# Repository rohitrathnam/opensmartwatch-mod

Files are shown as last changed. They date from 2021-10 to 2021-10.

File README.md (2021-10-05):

# opensmartwatch-mod
openSmartwatch project with an ECG frontend 

Part of course lab Electronic System Design

See Report.pdf for more details.

## Schematic
schematics

## PCB
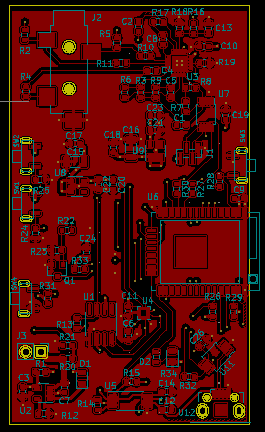
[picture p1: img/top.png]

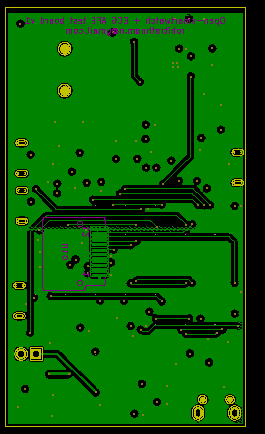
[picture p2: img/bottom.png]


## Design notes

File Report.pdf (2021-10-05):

# IL2237 Lab2 - PCB Design

### Rohit Rathnam Nareshkumar

### May 21, 2021

## 1 Introduction

The aim was to create a development board with the following features:

- A display and buttons to interact with the device
- WiFi / Bluetooth connectivity
- Battery powered with USB charging
- Compact ECG measurement
- Real time clock to keep track of time
- Accelerometer to help with ECG signal processing

The base schematic design that this project is built on is the Open-SmartWatch (OSW) project (1).

## 2 Schematic Design

The Open-SmartWatch schematic is based on an ESP-32 module with support for all of the above except the ECG module. The base schematic is given in Fig 1.
The modified schematic with the ECG circuit is given in Fig 2. The ECG circuit is based on reference design from AD8232 ECG analog front end IC and ADS1015 12-bit ADC.

1

Figure 1: Original schematic

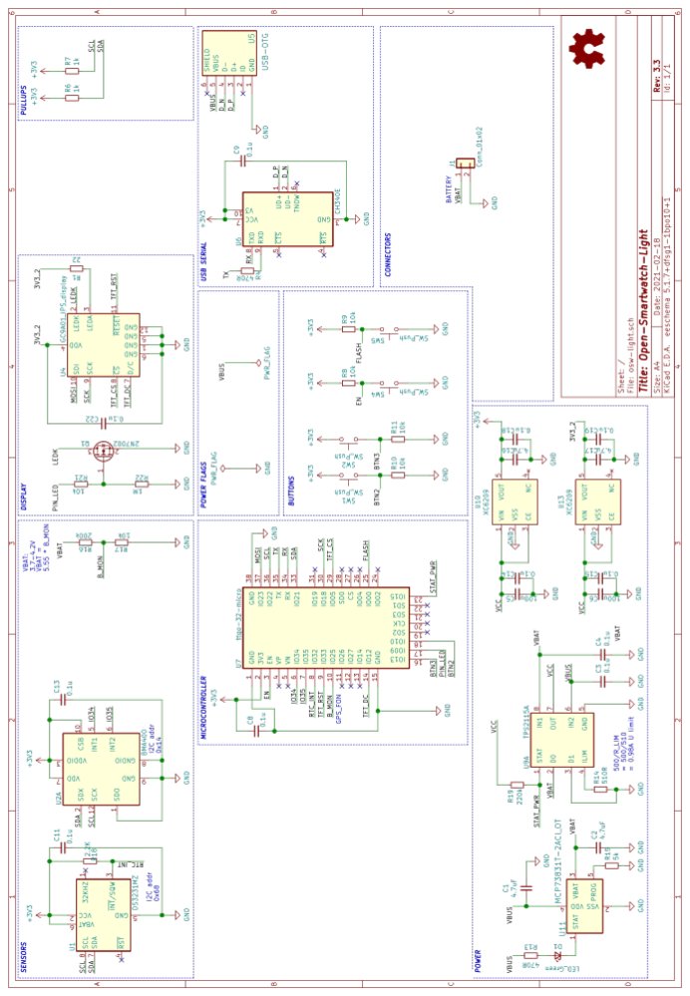
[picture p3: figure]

2

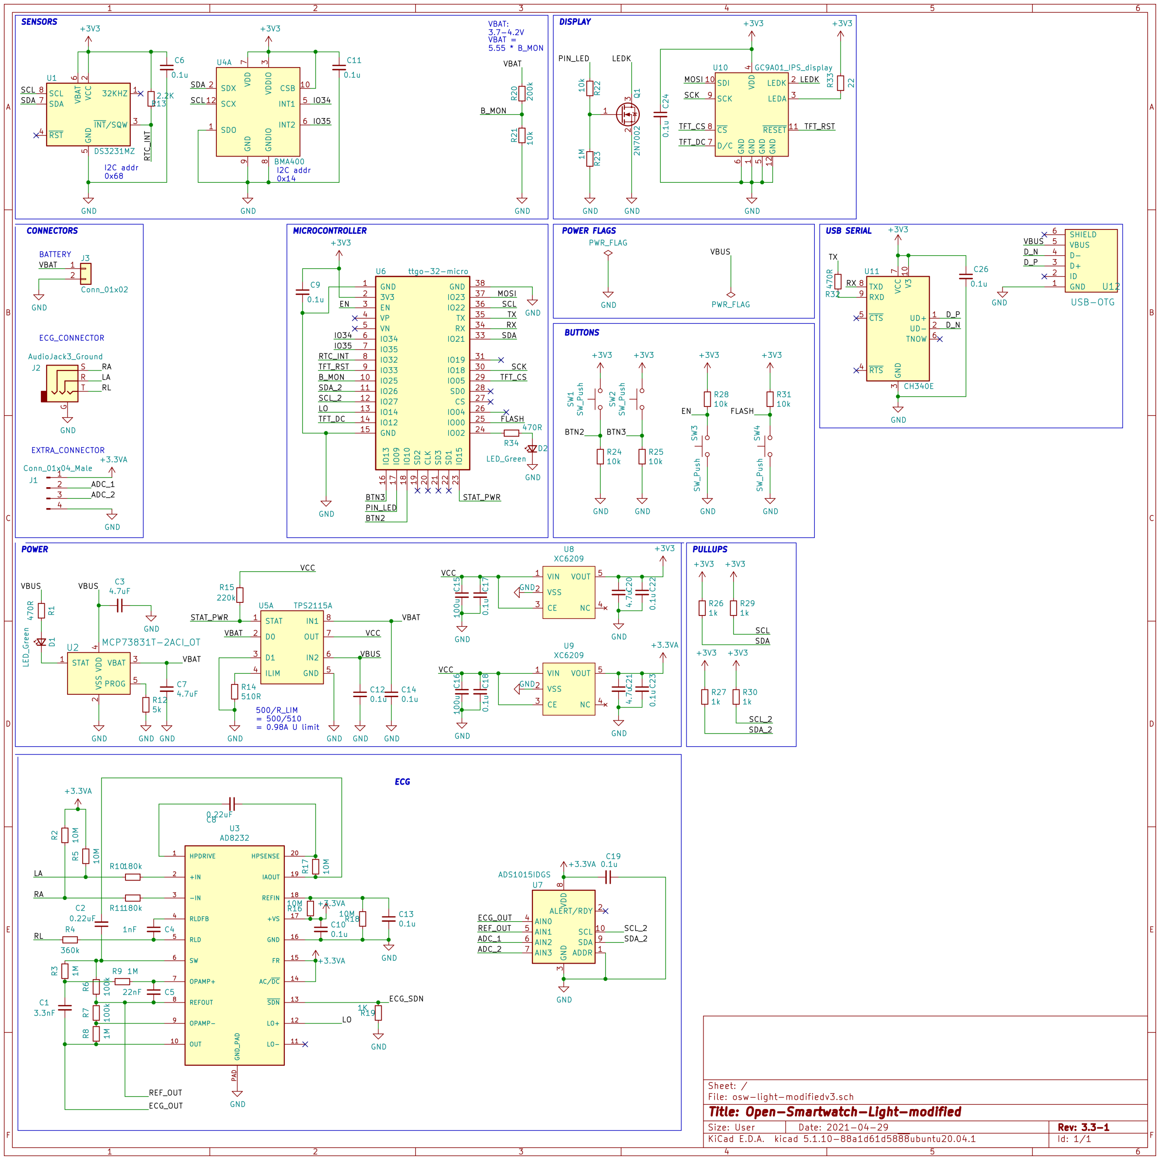
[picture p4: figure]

Figure 2: Modified schematic

3

### 2.1 Microcontroller

The microcontroller used in this project is an ESP-32 variant called the ttgo-32, which has a smaller form factor suitable for smartwatches. It has a PCB antenna and support for WiFi / Bluetooth. The microcontroller also features a low power core, which can be utilised to improve battery life when logging data. The PCB antenna is positioned extending from the edge of the board so that the copper does not interfere with the transmission line. The programming interface is through USB, the device goes into programming mode using the BOOT push button.

### 2.2 Power supply

The power supply consists of a battery management IC (MCP73831) which is responsible for charging the single cell Li battery, current limiting the battery, and producing a regulated output (VBUS). A power line multiplexer (TPS2115A) is used to switch between battery power and USB 5V. The output voltage then goes to two parallel voltage regulators (XC6209) which produce 3V3 and A3V3. Net 3V3 powers all the digital circuits, and A3V3 powers the ECG front end module and ADC. The original design had the display on a separate voltage regulator (possibly due to higher power consumption), but to accommodate a separate analog supply rail, the display was shifted to the digital supply regulator along with the other peripherals and micro-controller. The device can also monitor battery voltage through a voltage divider connected to the internal ADC of the ESP-32.

### 2.3 Display

The display module is a circular IPS display which interfaces over SPI. The module has a FPC connector which is placed on the back of the board to fold the display over the board.

### 2.4 Peripherals

The other peripherals include a BMA400 accelerometer, and a real-time clock both connected via I2C to the ESP-32. Push buttons were given for boot, turning on display and two buttons with software defined functions. A power LED

4

### 2.5 ECG module and ADC

The ECG module (AD8232) and 12-bit ADC (ADS1015) are powered by A3V3 net. The input to the ECG module is through a 3-pin 3.5mm audio jack interface. This can connect to an off the shelf module for ECG leads (2). The design for this section was adapted from the application note given in the datasheet (3). The ECG module has a differential output, which is connected to the two of the ADC input pins. Additional safety mechanism such as ESD diodes, fuses etc. were ignored due to additional complexity in schematic design, which was beyond the scope of this lab. The two extra inputs to the ADC were broken out along with A3V3 and GND to a 1mm pin header for future use. The ADC interfaces with the microcontroller over I2C, and was connected to a dedicated I2C pins so the accelerometer and ADC readings can be polled simultaneously do aid ECG signal processing and motion noise removal.

## 3 Layout considerations

The major factors considered was in the placement of USB connector and routing of USB differential pair, proper clearance for the antenna section of the ESP-32, and proper routing and placement of components for the ECG IC and ADC. For this design, I decided to go with a 4 layer board to allow for ground and power planes. Since this was a development board, there is not much size constraint, as such I tried to stick with a credit card size as a starting point. The final dimensions of the board is 70mm x 40mm.

### 3.1 Component placement

- Priority was given to routing the differential pair to the USB IC from the connector at the edge of the board. The traces were calculated using the KiCAD PCBcalculator tool shown in Fig. 4.
- Decoupling capacitors for all of the devices were placed as close as possible to the supply pins and vias connected to the respective layers.
- The ECG IC and the ADC were placed in a separate section of the board to minimise noise. A split ground plane was avoided for simplicity. The trace length and layer changes were minimised as much as possible.
- Signal traces were 0.25mm wide and power traces were 0.5mm / 1mm

5

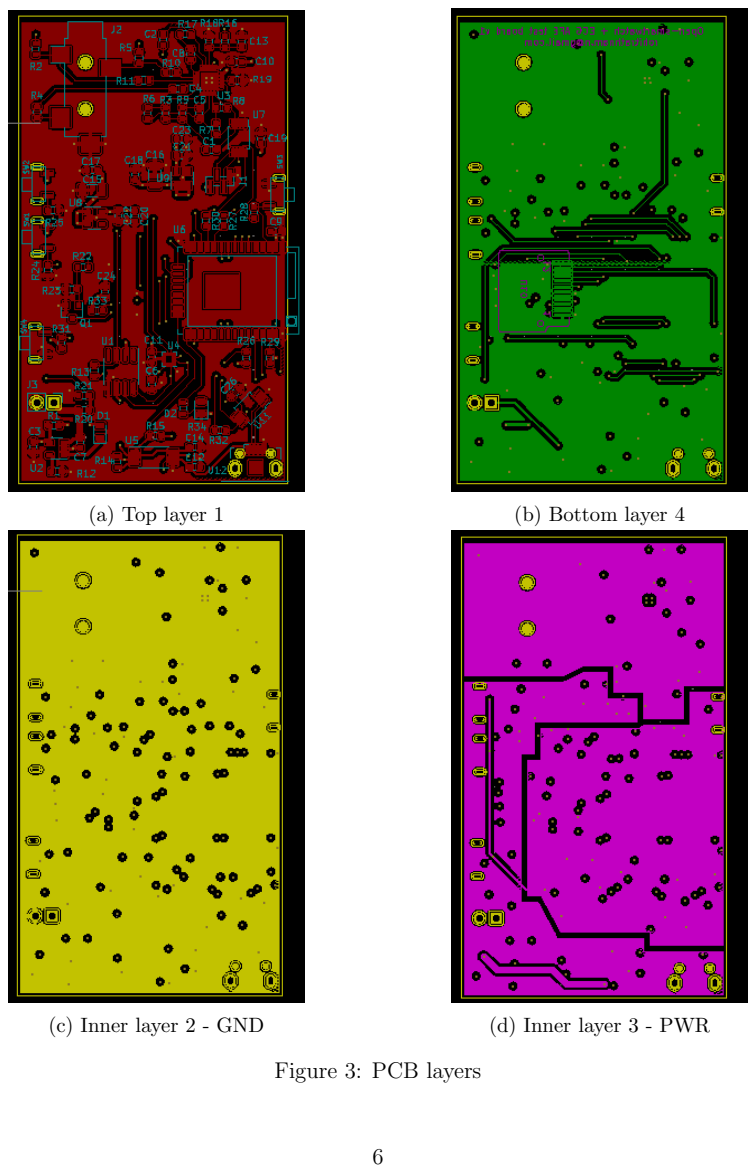
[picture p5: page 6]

(a) Top layer 1 | (b) Bottom layer 4
(c) Inner layer 2 - GND | (d) Inner layer 3 - PWR

Figure 3: PCB layers

6

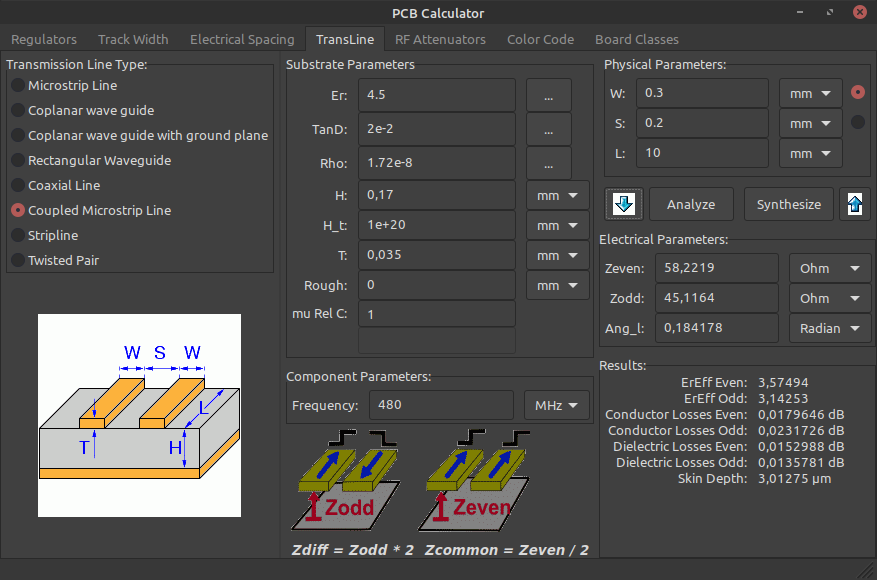
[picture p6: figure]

Figure 4: Differential pair trace impedance calculation

traces depending on the pad size. Routing under components was minimised as much as possible.

### 3.2 PCB Layers and routing

Refer Fig 3 for individual layers.

### 3.2.1 Top Layer 1

The top layer consists of all the components except the FPC connector for the display. Most of the routing to nearby components and long vertical traces were kept in the top layer.

### 3.2.2 Bottom Layer 4

The bottom layer consists of mainly of the FPC connector for the display long horizontal traces. The rest was polygon filled with GND.

7

### 3.2.3 Inner Layer 2

This layer consists of the ground plane. Care was taken to minimize or avoid slots in the ground plane under components and high frequency traces (SPI, I2C, USB).

### 3.2.4 Inner Layer 3

This layer was used for routing power. 3 fill zones were created - consisting of 3V3 (digital supply), A3V3 (analog supply) and VCC (supply to regulators). The slots created in this layer might lead to electromagnetic emission, but most of the slots area is covered by the GND fill from other layers to mitigate this.

### 3.3 Fabrication Outputs

The results of the DRC are shown in Fig.5. The Gerber files are attached to this submission, which was verified with the SeedStudio Gerber viewer as shown in Fig. 6. The bill of materials csv file and ibom.html is also included in the submitted zip folder.

## References

[1] P. Smith, “Open-smartwatch.” https://open-smartwatch.github.io/. Accessed on 2021-05-20.
[2] SparkFun, | “Sparkfun | sensor | cable | accessory.”
https://www.sparkfun.com/products/12970. | Accessed on 2021-05-
20.
[3] AnalogDevices, “Ad8232 datasheet.” https://www.analog.com/media/en/technicaldocumentation/data-sheets/ad8232.pdf. Accessed on 2021-05-20.

8

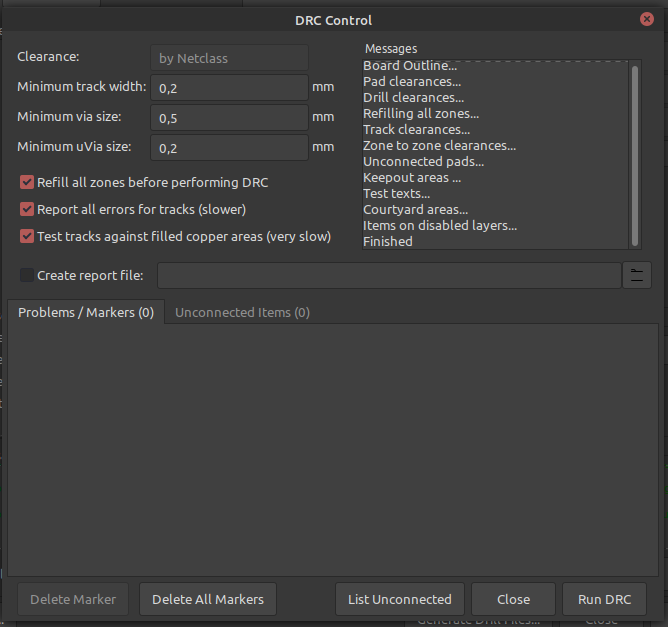
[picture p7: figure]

Figure 5: DRC results

9

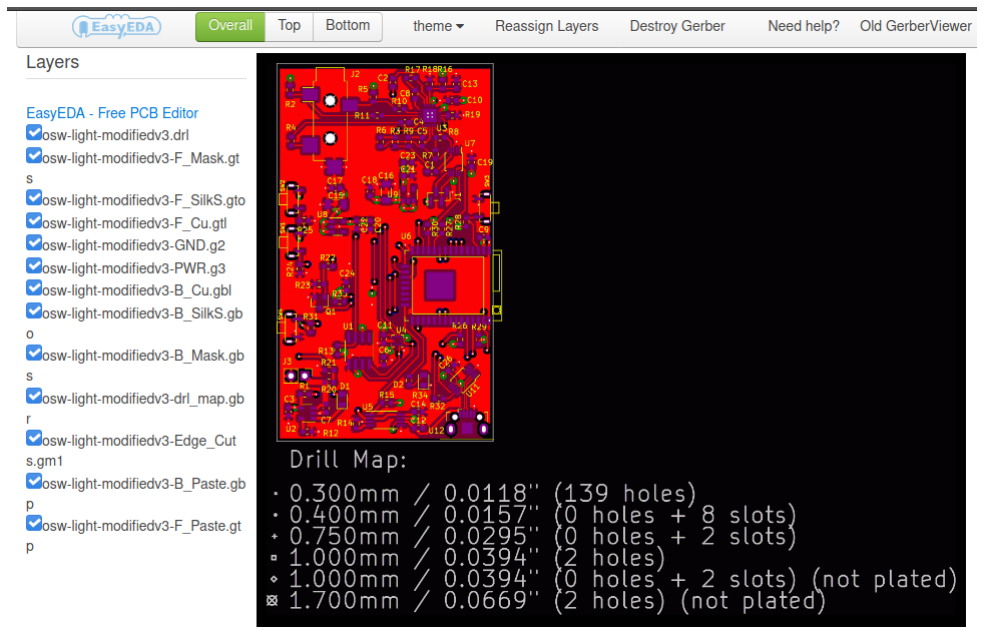
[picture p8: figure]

Figure 6: Seedstudio Gerber viewer

10

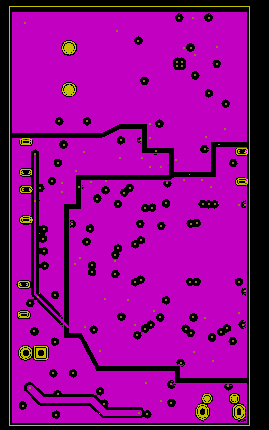
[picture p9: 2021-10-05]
img/PWR.png

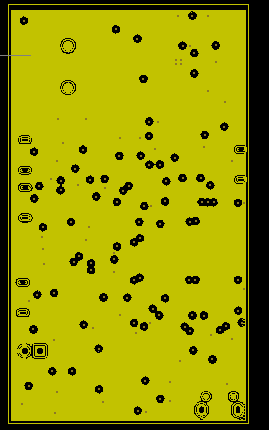
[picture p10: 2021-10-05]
img/GND.png

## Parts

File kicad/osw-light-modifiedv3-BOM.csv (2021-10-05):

Reference | Quantity | Value | Footprint | Vendor_PN | Vendor
C1 | 1 | 3.3nF | Capacitor_SMD:C_0603_1608Metric | 2904841 | Farnell
C6 C9 C10 C11 C12 C13 C14 C17 C18 C19 C22 C23 C24 C26 | 14 | 0.1u | Capacitor_SMD:C_0603_1608Metric | 1414027 | Farnell
C15 C16 | 2 | 100u | Capacitor_SMD:C_1206_3216Metric | 2852714 | Farnell
C2 C8 | 2 | 0.22uF | Capacitor_SMD:C_0603_1608Metric | 2905025 | Farnell
C20 C21 | 2 | 4.7u | Capacitor_SMD:C_0603_1608Metric | 3217549 | Farnell
C4 | 1 | 1nF | Capacitor_SMD:C_0603_1608Metric | 1414025 | Farnell
C5 | 1 | 22nF | Capacitor_SMD:C_0603_1608Metric | 1520257 | Farnell
C3 C7 | 2 | 4.7uF | Capacitor_SMD:C_0603_1608Metric | 3217549 | Farnell
D1 D2 | 2 | LED_Green | LED_SMD:LED_0805_2012Metric | 2290331 | Farnell
J1 | 1 | Conn_01x04_Male | Connector_PinHeader_1.00mm:PinHeader_1x04_P1.00mm_Vertical_SMD_Pin1Left
J2 | 1 | AudioJack3_Ground | open-Smartwatch:Jack_3.5mm_CUI_SJ-3524-SMT_Horizontal_mod | 2915138 | Farnell
J3 | 1 | Conn_01x02 | Connector_PinHeader_2.54mm:PinHeader_1x02_P2.54mm_Vertical
Q1 | 1 | 2N7002 | Package_TO_SOT_SMD:SOT-23 | https://www.aliexpress.com/item/32912312094.html | Aliexpress
R1 R32 R34 | 3 | 470R | Resistor_SMD:R_0603_1608Metric | 2331232 | Farnell
R10 R11 | 2 | 180k | Resistor_SMD:R_0603_1608Metric | 2447266 | Farnell
R12 | 1 | 5k | Resistor_SMD:R_0603_1608Metric | PNM0603-5.0KBCT-ND | Digikey
R13 | 1 | 2.2K | Resistor_SMD:R_0603_1608Metric | 2303166 | Farnell
R14 | 1 | 510R | Resistor_SMD:R_0603_1608Metric | 2447392 | Farnell
R15 | 1 | 220k | Resistor_SMD:R_0603_1608Metric | 2447297 | Farnell
R19 | 1 | 1K | Resistor_SMD:R_0603_1608Metric | 3495238 | Farnell
R20 | 1 | 200k | Resistor_SMD:R_0603_1608Metric | 2447291 | Farnell
R3 R8 R9 R23 | 4 | 1M | Resistor_SMD:R_0603_1608Metric | 2331023 | Farnell
R21 R22 R24 R25 R28 R31 | 6 | 10k | Resistor_SMD:R_0603_1608Metric | 3495224 | Farnell
R26 R27 R29 R30 | 4 | 1k | Resistor_SMD:R_0603_1608Metric | 3495238 | Farnell
R33 | 1 | 22 | Resistor_SMD:R_0603_1608Metric | 2447301 | Farnell
R4 | 1 | 360k | Resistor_SMD:R_0603_1608Metric | 3495822 | Farnell
R2 R5 R16 R17 R18 | 5 | 10M | Resistor_SMD:R_0603_1608Metric | 2138612 | Farnell
R6 R7 | 2 | 100k | Resistor_SMD:R_0603_1608Metric | 3495222 | Farnell
SW1 SW2 SW3 SW4 | 4 | SW_Push | open-Smartwatch:button_side_smd | https://www.aliexpress.com/item/32870278366.html | Aliexpress
U1 | 1 | DS3231MZ | Package_SO:SOIC-8_3.9x4.9mm_P1.27mm | https://www.aliexpress.com/item/32962505279.html | Aliexpress
U10 | 1 | GC9A01_IPS_display | open-Smartwatch:GC9A01_IPS_display | https://www.aliexpress.com/item/1005001382307998.html | Aliexpress
U11 | 1 | CH340E | open-Smartwatch:MSOP-10_3x3mm_P0.5mm | https://www.aliexpress.com/item/4000171821951.html | Aliexpress
U12 | 1 | USB-OTG | open-Smartwatch:USBmicro-B | https://www.aliexpress.com/item/32820570603.html | Aliexpress
U2 | 1 | MCP73831T-2ACI_OT | open-Smartwatch:SOT-23-5 | 2857755 | Farnell
U3 | 1 | AD8232 | LFCSP_20 | AD8232ACPZ-R7CT-ND | Digikey
U4 | 1 | BMA400 | open-Smartwatch:LGA-12_2x2mm_P0.5mm | 828-1081-1-ND | Digikey
U5 | 1 | TPS2115A | open-Smartwatch:TSSOP-8_4.4x3mm_P0.65mm | 3124061 | Farnell
U6 | 1 | ttgo-32-micro | open-Smartwatch:ttgo-32-micro | https://www.aliexpress.com/item/32869180373.html | Aliexpress
U7 | 1 | ADS1015IDGS | Package_SO:TSSOP-10_3x3mm_P0.5mm | 3004281 | Farnell
U8 U9 | 2 | XC6209 | Package_TO_SOT_SMD:SOT-23-5 | 3535214 | Farnell
BAT | 1 |  |  | https://a.aliexpress.com/_mrvOz8P | Aliexpress

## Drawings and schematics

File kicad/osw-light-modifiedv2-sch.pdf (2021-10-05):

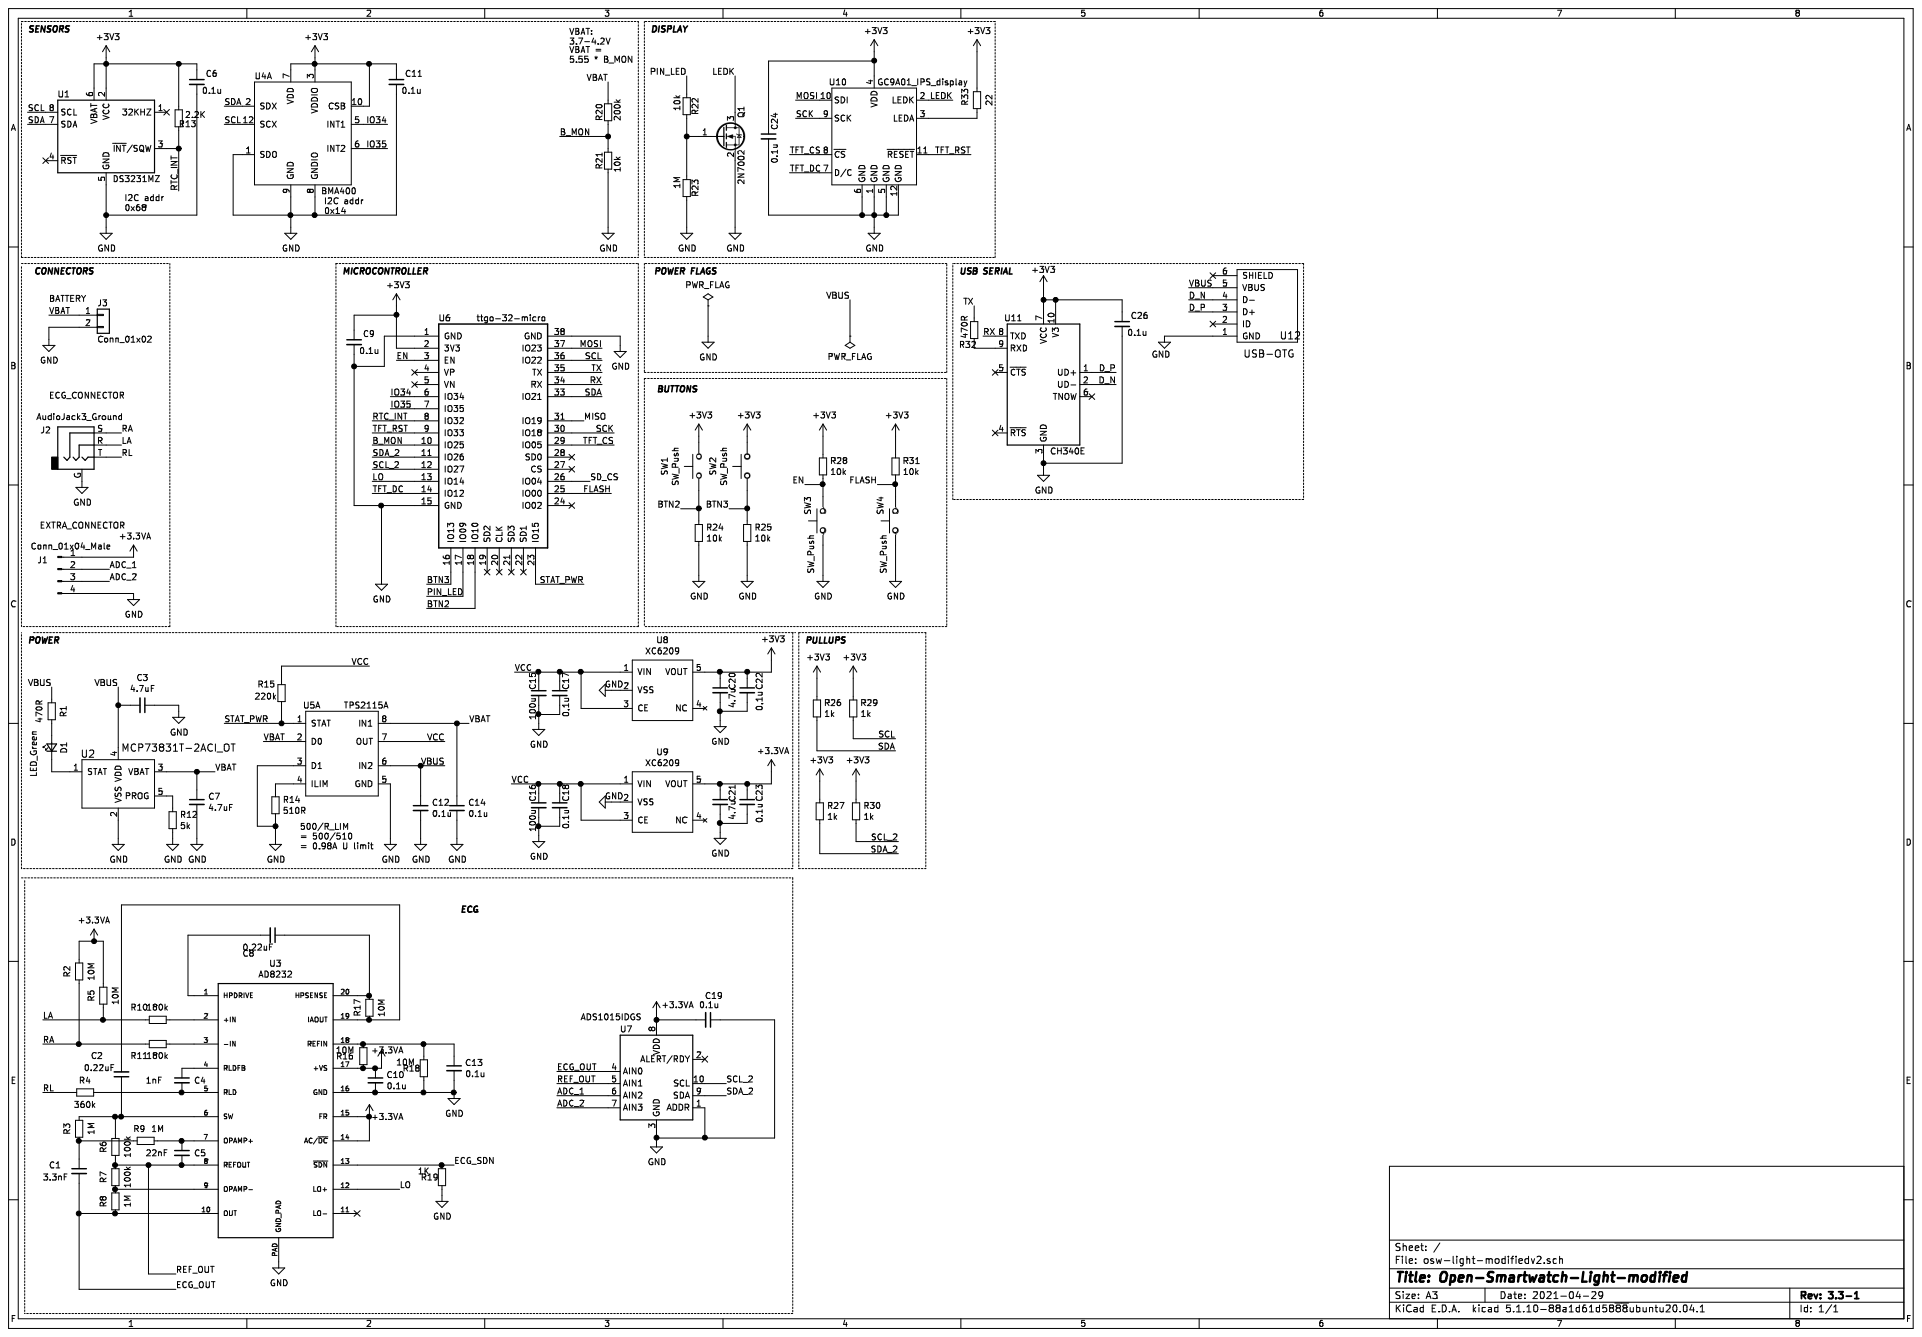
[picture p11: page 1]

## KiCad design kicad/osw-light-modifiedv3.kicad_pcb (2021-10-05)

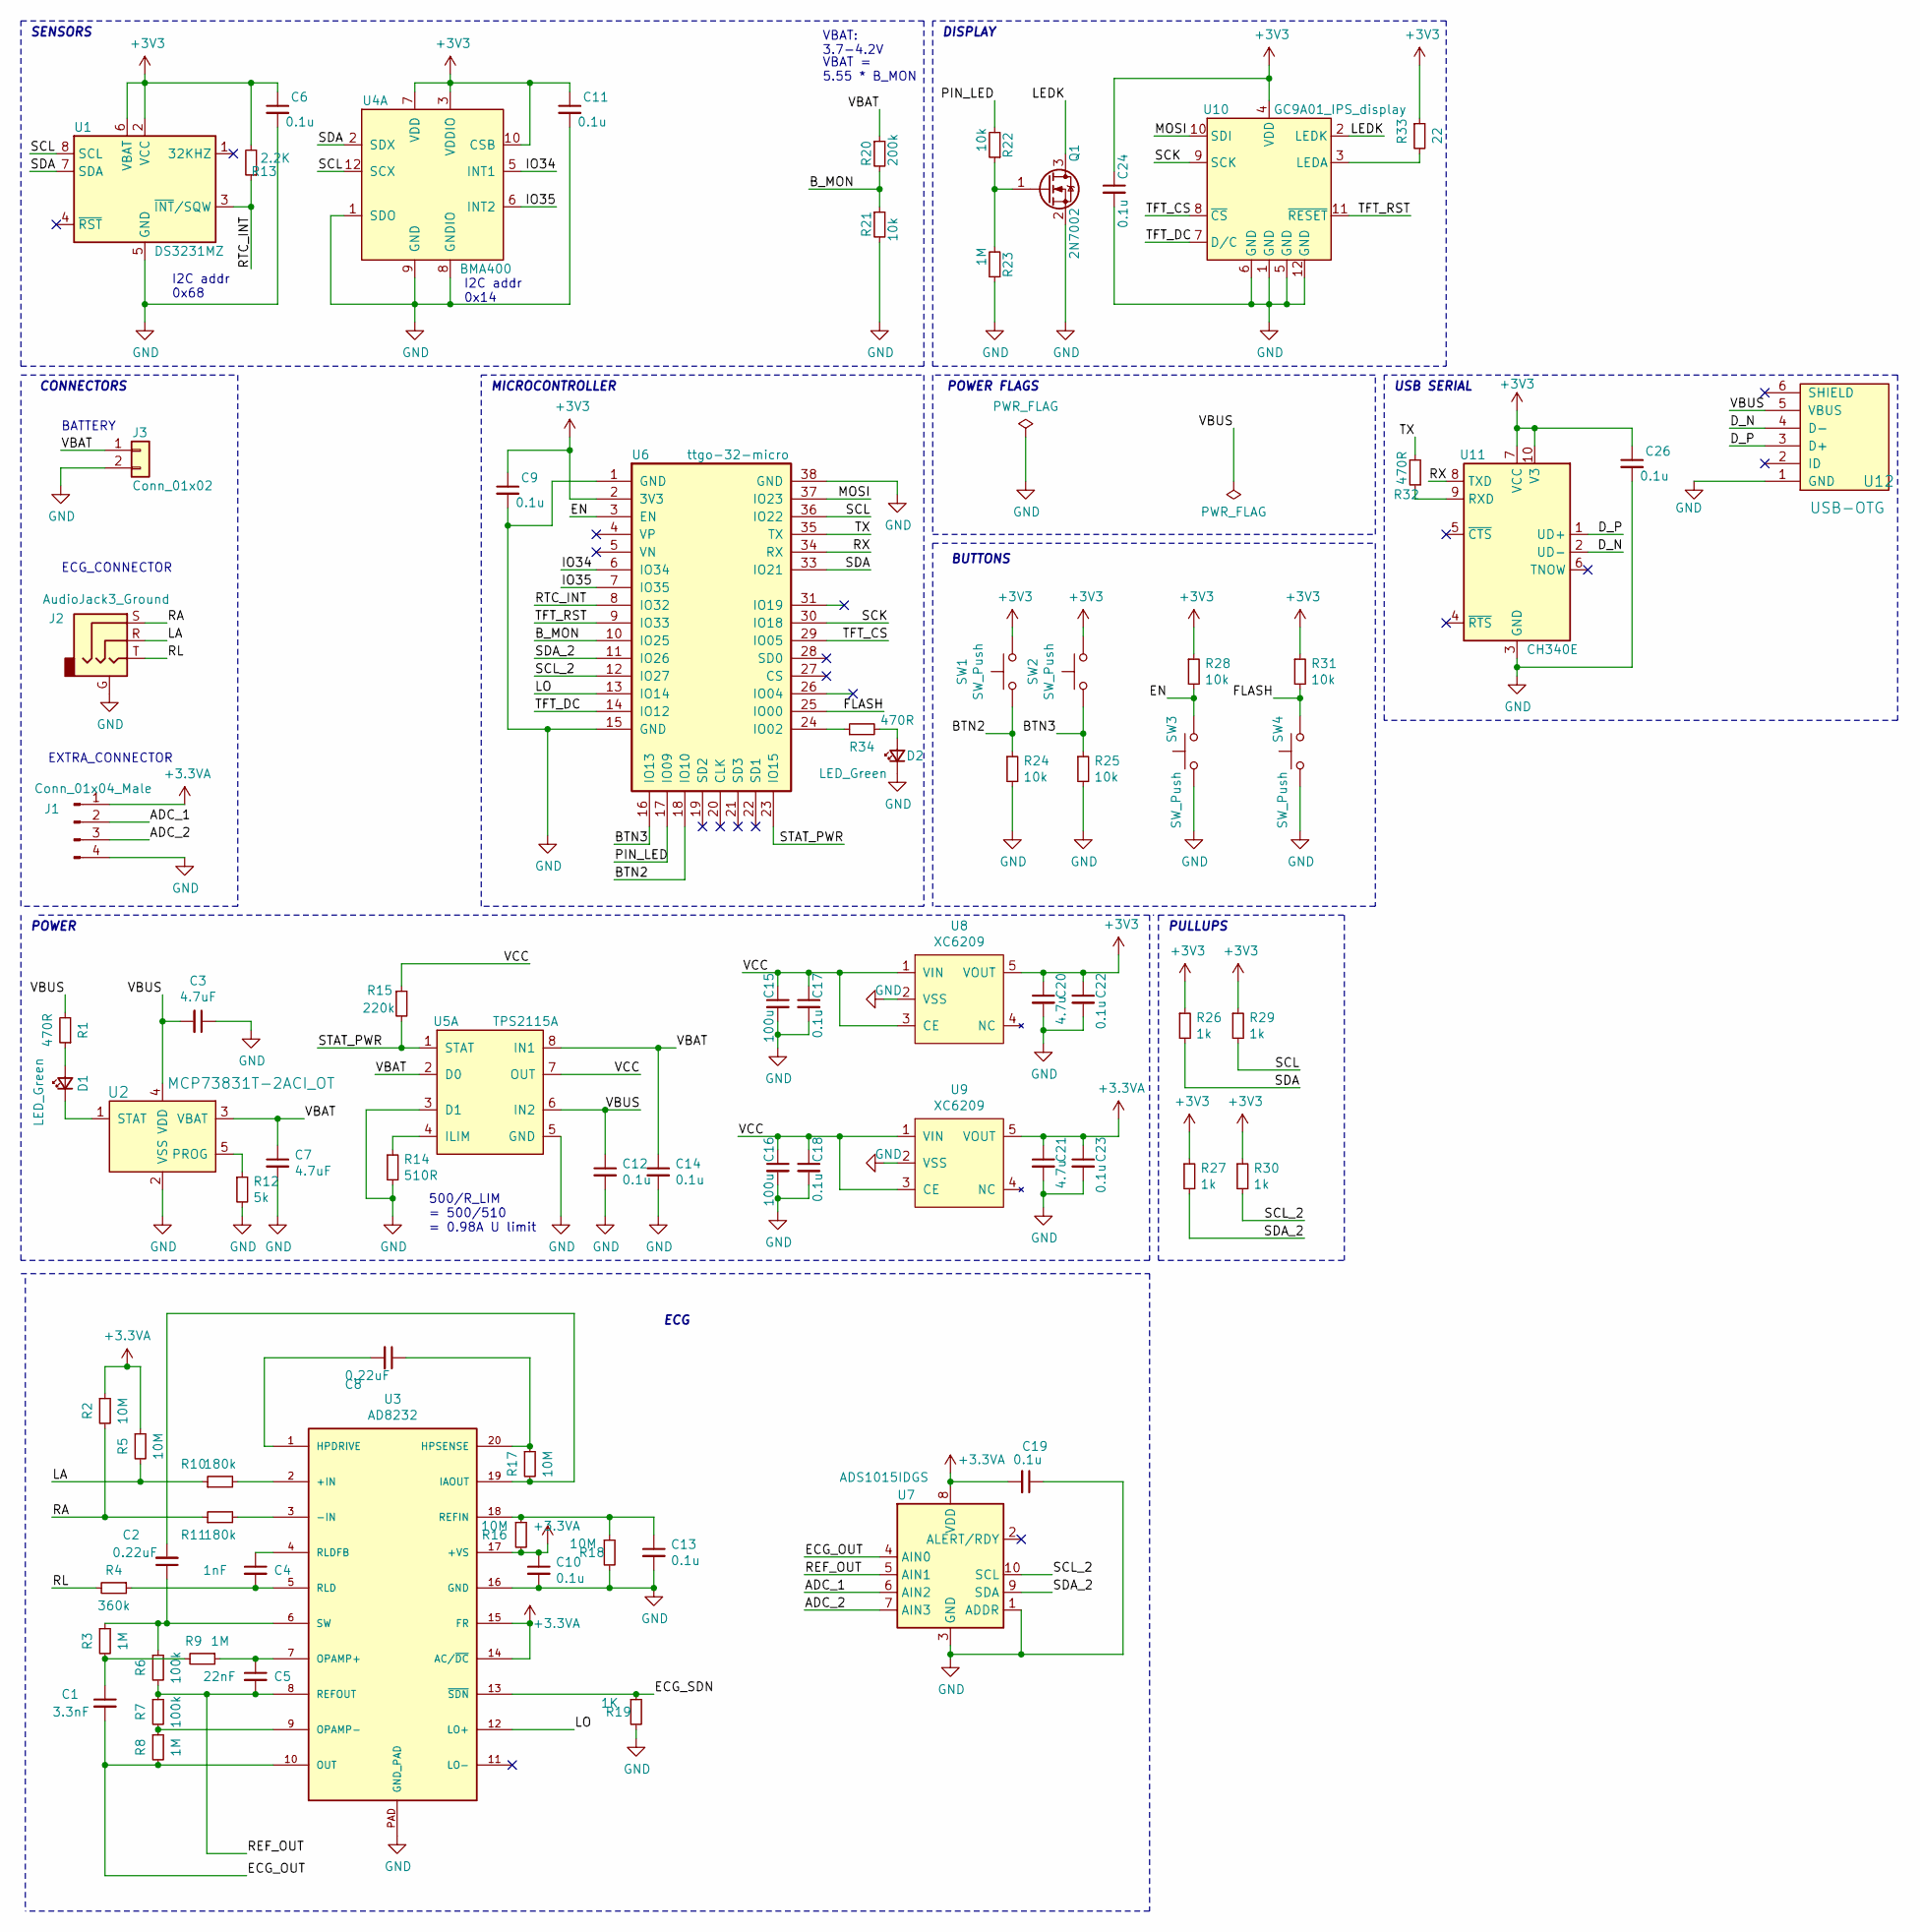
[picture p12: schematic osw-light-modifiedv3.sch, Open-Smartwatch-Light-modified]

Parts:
C1: 3.3nF; C_0603_1608Metric
C2, C8: 0.22uF; C_0603_1608Metric
C3, C7: 4.7uF; C_0603_1608Metric
C4: 1nF; C_0603_1608Metric
C5: 22nF; C_0603_1608Metric
C6, C9, C10, C11, C12, C13, C14, C17, C18, C19, C22, C23, C24, C26: 0.1u; C_0603_1608Metric
C15, C16: 100u; C_1206_3216Metric
C20, C21: 4.7u; C_0603_1608Metric
D1, D2: LED_Green; LED_0805_2012Metric
J1: Conn_01x04_Male; PinHeader_1x04_P1.00mm_Vertical_SMD_Pin1Left
J2: AudioJack3_Ground; Jack_3.5mm_CUI_SJ-3524-SMT_Horizontal_mod
J3: Conn_01x02; PinHeader_1x02_P2.54mm_Vertical
Q1: 2N7002; SOT-23
R1, R32, R34: 470R; R_0603_1608Metric
R2, R5, R16, R17, R18: 10M; R_0603_1608Metric
R3, R8, R9, R23: 1M; R_0603_1608Metric
R4: 360k; R_0603_1608Metric
R6, R7: 100k; R_0603_1608Metric
R10, R11: 180k; R_0603_1608Metric
R12: 5k; R_0603_1608Metric
R13: 2.2K; R_0603_1608Metric
R14: 510R; R_0603_1608Metric
R15: 220k; R_0603_1608Metric
R19: 1K; R_0603_1608Metric
R20: 200k; R_0603_1608Metric
R21, R22, R24, R25, R28, R31: 10k; R_0603_1608Metric
R26, R27, R29, R30: 1k; R_0603_1608Metric
R33: 22; R_0603_1608Metric
SW1, SW2, SW3, SW4: SW_Push; button_side_smd
U1: DS3231MZ; SOIC-8_3.9x4.9mm_P1.27mm
U2: MCP73831T-2ACI_OT; SOT-23-5; MPN MCP73831T-2ACI/OT; Digi-Key_PN MCP73831T-2ACI/OTCT-ND
U3: AD8232; LFCSP_20
U4: BMA400; LGA-12_2x2mm_P0.5mm; MPN BMA400; DigiKey_PN 828-1081-1-ND
U5: TPS2115A; TSSOP-8_4.4x3mm_P0.65mm; MPN TPS2115APWR; DigiKey_PN 296-16940-1-ND
U6: ttgo-32-micro
U7: ADS1015IDGS; TSSOP-10_3x3mm_P0.5mm
U8, U9: XC6209; SOT-23-5
U10: GC9A01_IPS_display
U11: CH340E; MSOP-10_3x3mm_P0.5mm
U12: USB-OTG; USBmicro-B

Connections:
+3.3VA: C10.1, C19.2, C21.1, C23.1, J1.1, R2.1, R5.1, R16.2, U3.14 (AC/~DC), U3.15 (FR), U3.17 (+VS), U7.8 (VDD), U9.5 (VOUT)
+3V3: C6.1, C9.1, C11.1, C20.1, C22.1, C24.1, C26.1, R13.2, R26.1, R27.1, R28.1, R29.1, R30.1, R31.1, R33.1, SW1.2, SW2.2, U1.2 (VCC), U1.6 (VBAT), U4.3 (VDDIO), U4.7 (VDD), U4.10 (CSB), U6.2 (3V3), U8.5 (VOUT), U10.4 (VDD), U11.7 (VCC), U11.10 (V3)
/ADC_1: J1.2, U7.6 (AIN2)
/ADC_2: J1.3, U7.7 (AIN3)
/BTN2: R24.1, SW1.1, U6.18 (IO10)
/BTN3: R25.1, SW2.1, U6.16 (IO13)
/B_MON: R20.2, R21.1, U6.10 (IO25)
/D_N: U11.2 (UD-), U12.4 (D-)
/D_P: U11.1 (UD+), U12.3 (D+)
/ECG_OUT: C1.2, R8.2, U3.10 (OUT), U7.4 (AIN0)
/ECG_SDN: R19.1, U3.13 (~SDN)
/EN: R28.2, SW3.2, U6.3 (EN)
/FLASH: R31.2, SW4.2, U6.25 (IO00)
/IO34: U4.5 (INT1), U6.6 (IO34)
/IO35: U4.6 (INT2), U6.7 (IO35)
/LA: J2.R, R5.2, R10.1
/LEDK: Q1.3 (D), U10.2 (LEDK)
/LO: U3.12 (LO+), U6.13 (IO14)
/MOSI: U6.37 (IO23), U10.10 (SDI)
/PIN_LED: R22.2, U6.17 (IO09)
/RA: J2.S, R2.2, R11.1
/REF_OUT: C5.2, R6.2, R7.1, U3.8 (REFOUT), U7.5 (AIN1)
/RL: J2.T, R4.2
/RTC_INT: R13.1, U1.3 (~INT~/SQW), U6.8 (IO32)
/RX: U6.34 (RX), U11.8 (TXD)
/SCK: U6.30 (IO18), U10.9 (SCK)
/SCL: R29.2, U1.8 (SCL), U4.12 (SCX), U6.36 (IO22)
/SCL_2: R30.2, U6.12 (IO27), U7.10 (SCL)
/SDA: R26.2, U1.7 (SDA), U4.2 (SDX), U6.33 (IO21)
/SDA_2: R27.2, U6.11 (IO26), U7.9 (SDA)
/STAT_PWR: R15.2, U5.1 (STAT), U6.23 (IO15)
/TFT_CS: U6.29 (IO05), U10.8 (~CS)
/TFT_DC: U6.14 (IO12), U10.7 (D/C)
/TFT_RST: U6.9 (IO33), U10.11 (~RESET)
/TX: R32.2, U6.35 (TX)
/VBAT: C7.1, C14.1, J3.1, R20.1, U2.3 (VBAT), U5.2 (D0), U5.8 (IN1)
/VBUS: C3.2, C12.1, R1.2, U2.4 (VDD), U5.6 (IN2), U12.5 (VBUS)
/VCC: C15.1, C16.1, C17.1, C18.1, R15.1, U5.7 (OUT), U8.1 (VIN), U8.3 (CE), U9.1 (VIN), U9.3 (CE)
GND: C3.1, C6.2, C7.2, C9.2, C10.2, C11.2, C12.2, C13.2, C14.2, C15.2, C16.2, C17.2, C18.2, C19.1, C20.2, C21.2, C22.2, C23.2, C24.2, C26.2, D2.1 (K), J1.4, J2.G, J3.2, Q1.2 (S), R12.2, R14.2, R18.2, R19.2, R21.2, R23.1, R24.2, R25.2, SW3.1, SW4.1, U1.5 (GND), U2.2 (VSS), U3.16 (GND), U3.PAD (GND_PAD), U4.1 (SDO), U4.8 (GNDIO), U4.9 (GND), U5.3 (D1), U5.5 (GND), U6.1 (GND), U6.15 (GND), U6.38 (GND), U7.1 (ADDR), U7.3 (GND), U8.2 (VSS), U9.2 (VSS), U10.1 (GND), U10.5 (GND), U10.6 (GND), U10.12 (GND), U11.3 (GND), U12.1 (GND)
unnamed: C1.1, R3.2, R9.2
unnamed: C2.1, R3.1, R6.1, U3.6 (SW)
unnamed: C2.2, R17.2, U3.19 (IAOUT)
unnamed: C4.1, U3.4 (RLDFB)
unnamed: C4.2, R4.1, U3.5 (RLD)
unnamed: C5.1, R9.1, U3.7 (OPAMP+)
unnamed: C8.1, R17.1, U3.20 (HPSENSE)
unnamed: C8.2, U3.1 (HPDRIVE)
unnamed: C13.1, R16.1, R18.1, U3.18 (REFIN)
unnamed: D1.1 (K), U2.1 (STAT)
unnamed: D1.2 (A), R1.1
unnamed: D2.2 (A), R34.2
unnamed: Q1.1 (G), R22.1, R23.2
unnamed: R7.2, R8.1, U3.9 (OPAMP-)
unnamed: R10.2, U3.2 (+IN)
unnamed: R11.2, U3.3 (-IN)
unnamed: R12.1, U2.5 (PROG)
unnamed: R14.1, U5.4 (ILIM)
unnamed: R32.1, U11.9 (RXD)
unnamed: R33.2, U10.3 (LEDA)
unnamed: R34.1, U6.24 (IO02)

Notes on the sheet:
500/R_LIM = 500/510 = 0.98A U limit
SENSORS
POWER
DISPLAY
USB SERIAL
BUTTONS
PULLUPS
BATTERY
VBAT: 3.7-4.2V
VBAT = 5.55 * B_MON
MICROCONTROLLER
POWER FLAGS
I2C addr 0x68
I2C addr 0x14
CONNECTORS
ECG_CONNECTOR
EXTRA_CONNECTOR
ECG

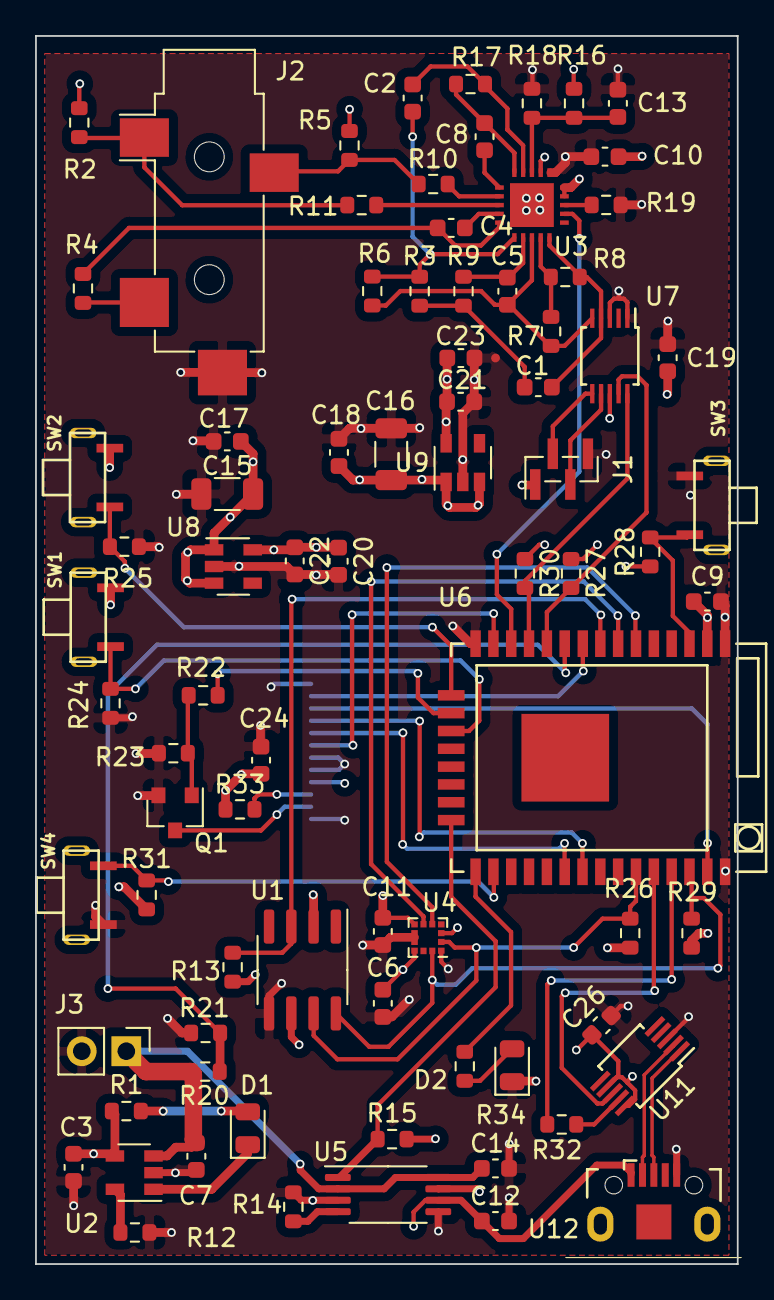
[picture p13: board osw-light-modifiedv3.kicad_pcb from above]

Board: 4 copper layers, 40.0 x 70.0 mm, 81 parts (1 on the bottom side), 60 nets.
